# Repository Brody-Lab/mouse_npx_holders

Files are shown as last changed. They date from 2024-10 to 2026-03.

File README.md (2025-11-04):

# The Tuckbox - neuropixel 2.0 holders for chronic electrophysiology in mice
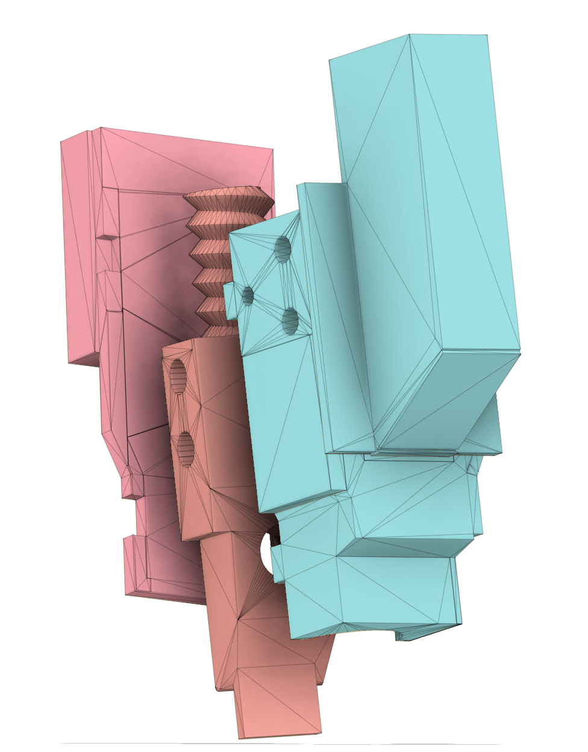
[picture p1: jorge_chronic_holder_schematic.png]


Printable files for Jesse Kaminsky's chronic neuropixel holders. All designs were modified in tinkercad from the original holders used for rats found in [this repo](https://github.com/agbondy/neuropixels_2.0_implant_assembly). Because of this I currently only have mesh files for these designs, and no true 3d structural file. Someday I'll learn an actual 3D modelling software...

Assembly instructions are [here](https://github.com/Brody-Lab/mouse_npx_holders/blob/main/Neuropixels%202.0%20Implant%20Assembly.pdf).

Production 2.0 internal holder modified in collaboration with [Rob Fetcho](https://scholar.google.com/citations?user=SHq1IlIAAAAJ&hl=en).

Narrower versions of production 2.0s by [Jorge Yanar](https://scholar.google.com/citations?user=Estf_eEAAAAJ&hl=en).

There is also a version of the [narrower holders with a cap](https://github.com/Brody-Lab/mouse_npx_holders/tree/main/production%20npx/npx2%20production%20narrow%20with%20cap), allowing complete protection of the probe/flex without any protective wrapping (for single-housed mice).

For other holders (that were designed for mice from the start) please see [this awesome resource](https://github.com/Julie-Fabre/awesome_neuropixels).

Feel free to contact me about these designs with any questions at jkaminsky@princeton.edu

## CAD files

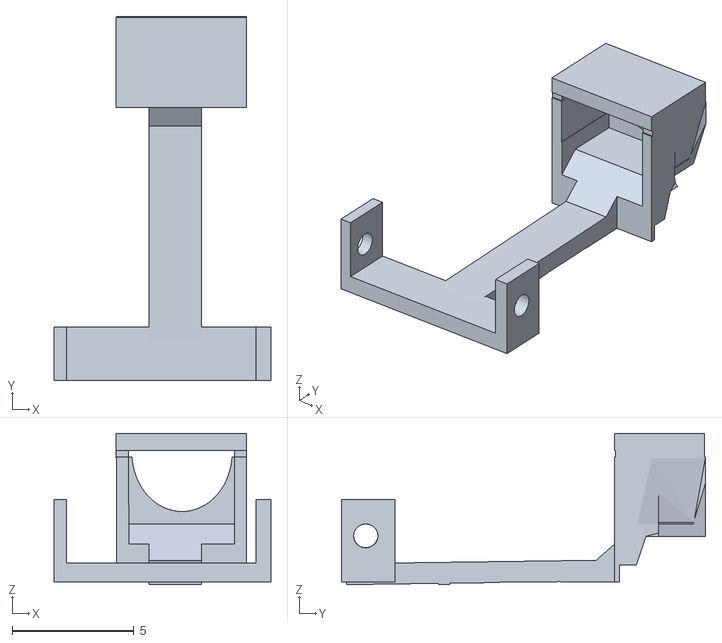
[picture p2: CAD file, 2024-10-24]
pre-production npx (phase 2b)/npx beta external frame.stl
8.90 x 14.9 x 6.20

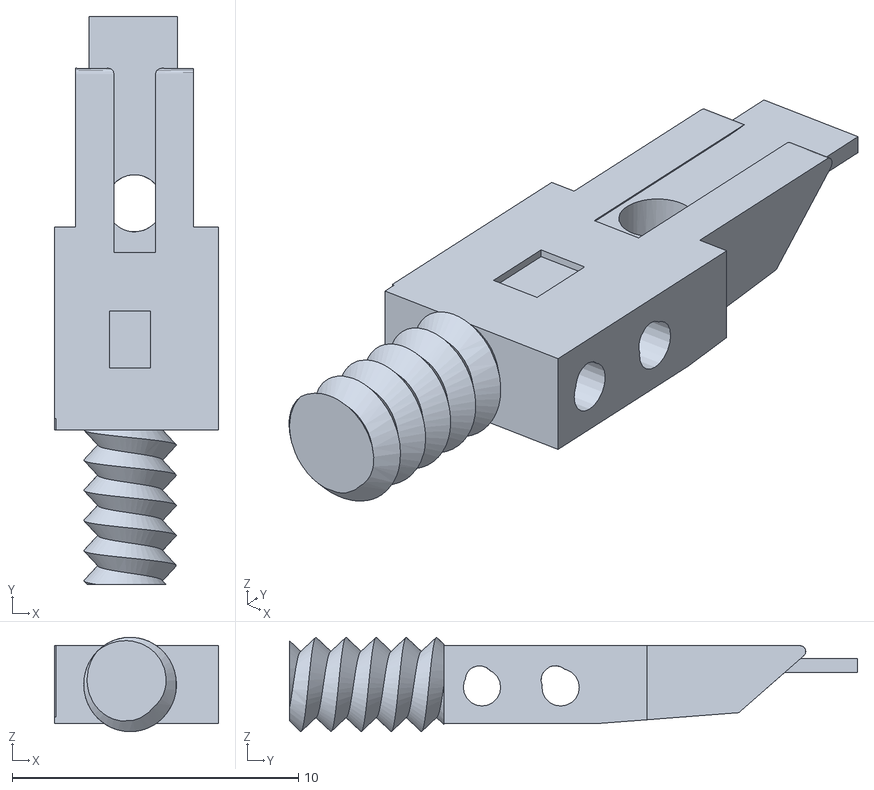
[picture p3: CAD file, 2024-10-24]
production npx/npx2 production internal jesse.stl
5.75 x 19.9 x 3.30

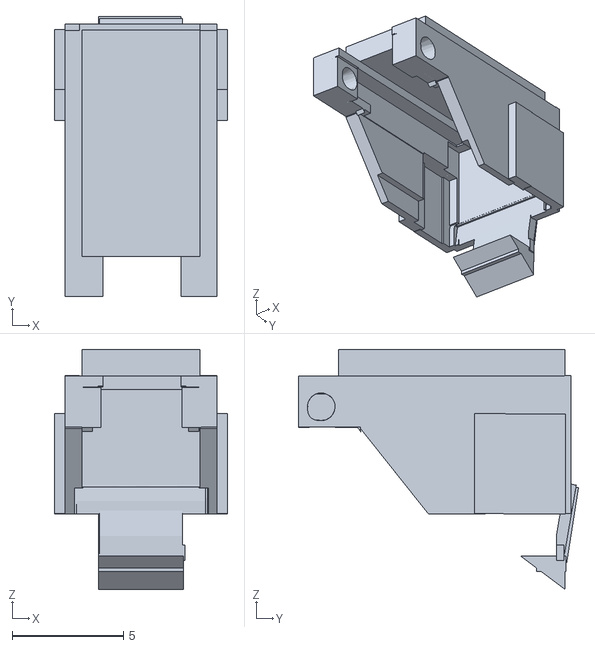
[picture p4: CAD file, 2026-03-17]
production npx/npx2 production narrow with cap/cap_v2.stl
7.80 x 12.6 x 10.8

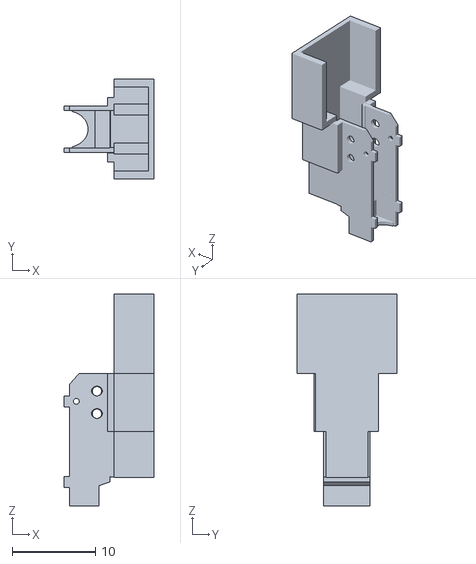
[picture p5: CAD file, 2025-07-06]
production npx/npx2 production narrow/Narrow production v6 external head stage.stl
10.8 x 12.0 x 25.4

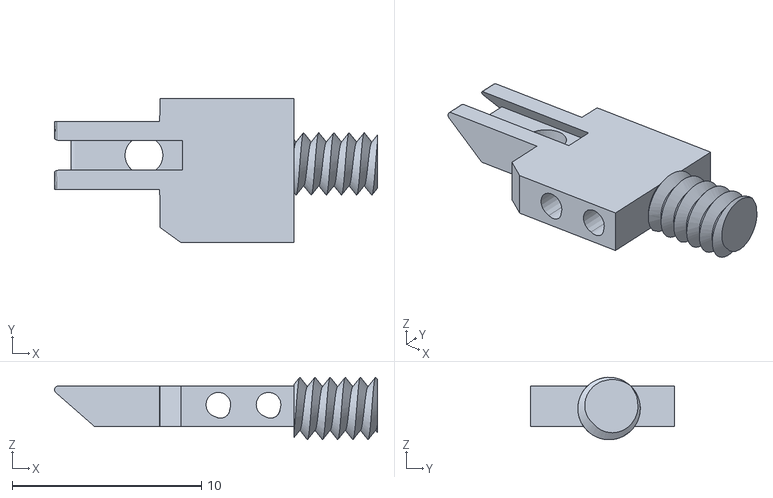
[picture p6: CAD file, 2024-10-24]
pre-production npx (phase 2b)/npx beta internal.stl
17.0 x 7.60 x 3.30

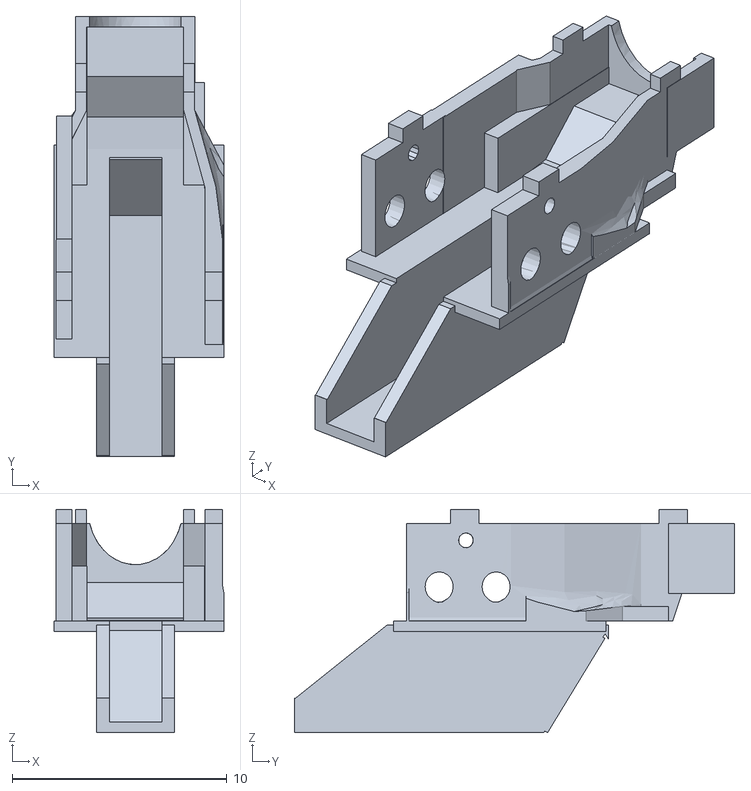
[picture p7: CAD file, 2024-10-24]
production npx/npx2 production external jesse.stl
7.90 x 20.5 x 10.4

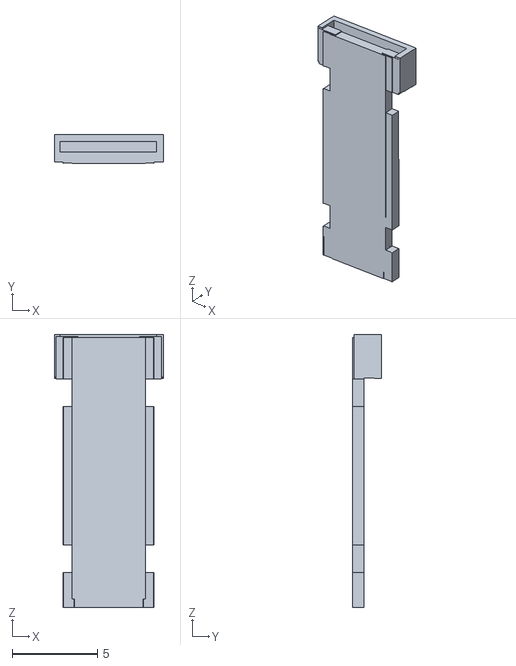
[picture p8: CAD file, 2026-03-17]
production npx/npx2 production narrow with cap/lid_v2.stl
6.40 x 1.70 x 16.0

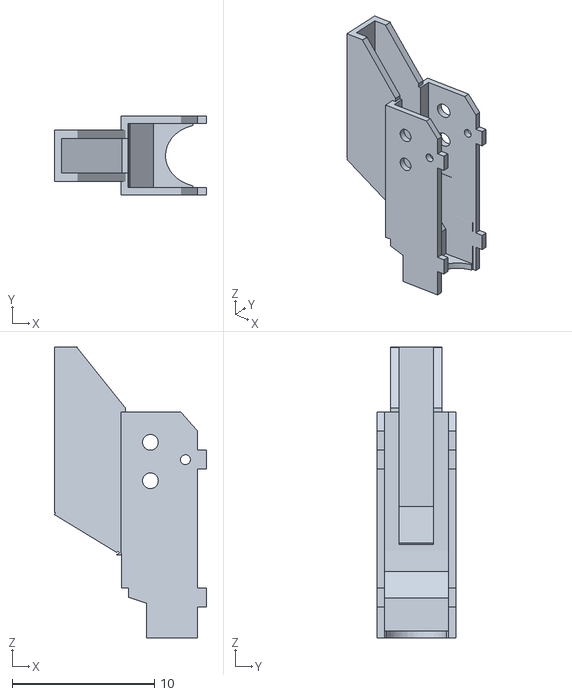
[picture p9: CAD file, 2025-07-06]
production npx/npx2 production narrow/Narrow production v6 external large tuckbox.stl
10.7 x 5.54 x 20.4

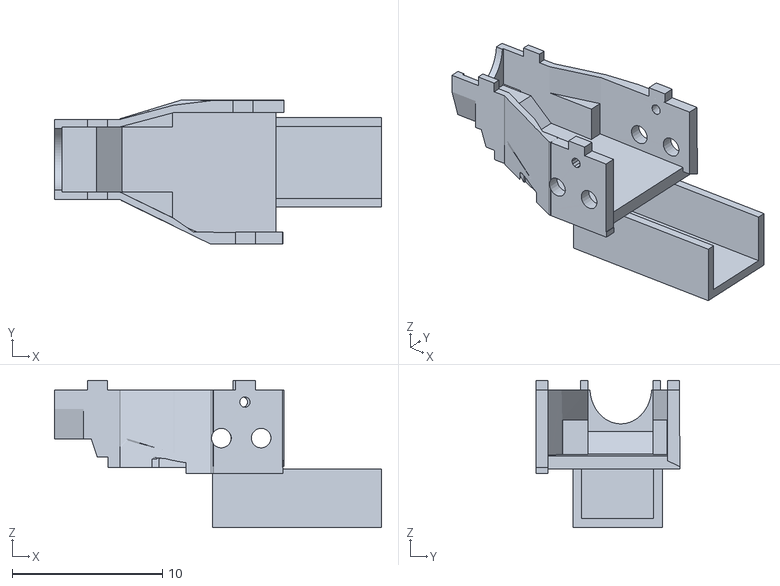
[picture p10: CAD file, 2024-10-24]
pre-production npx (phase 2b)/npx beta external.stl
21.7 x 9.60 x 9.79

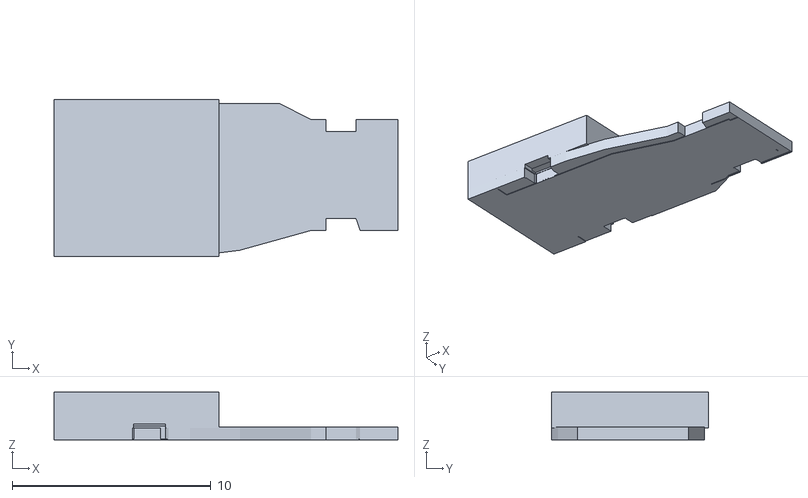
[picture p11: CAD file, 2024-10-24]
production npx/npx2 production lid jesse.stl
17.3 x 7.90 x 2.40

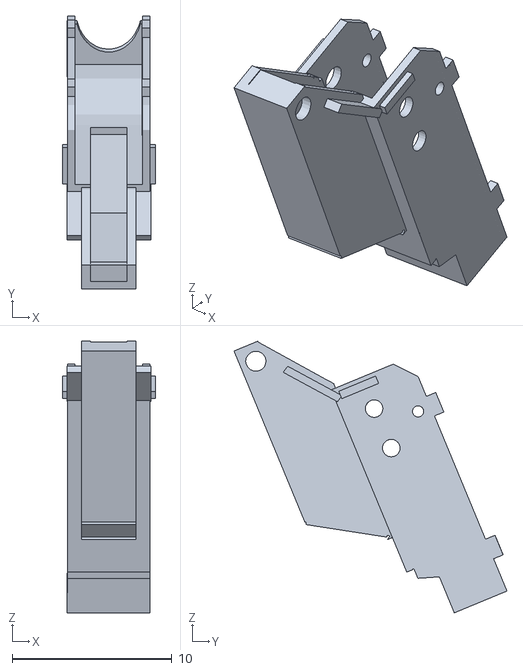
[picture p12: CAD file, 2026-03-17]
production npx/npx2 production narrow with cap/external_v2.stl
5.80 x 17.1 x 17.0

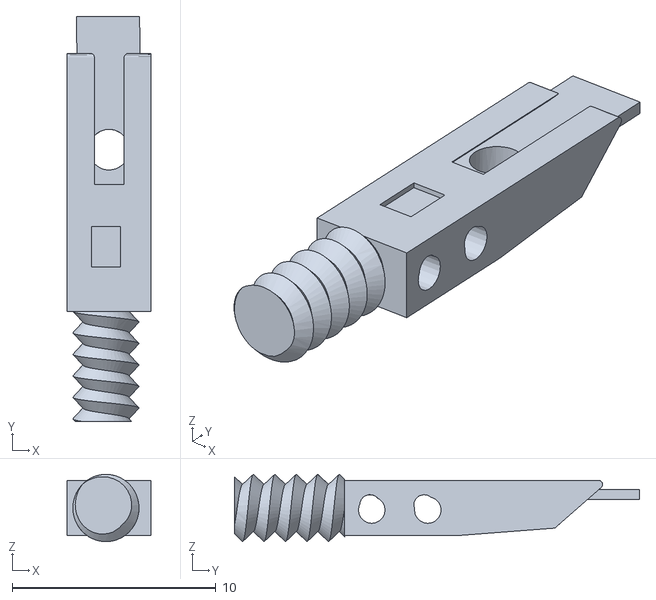
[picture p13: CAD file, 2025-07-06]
production npx/npx2 production narrow/Narrow production v7 internal.stl
4.12 x 19.9 x 3.30

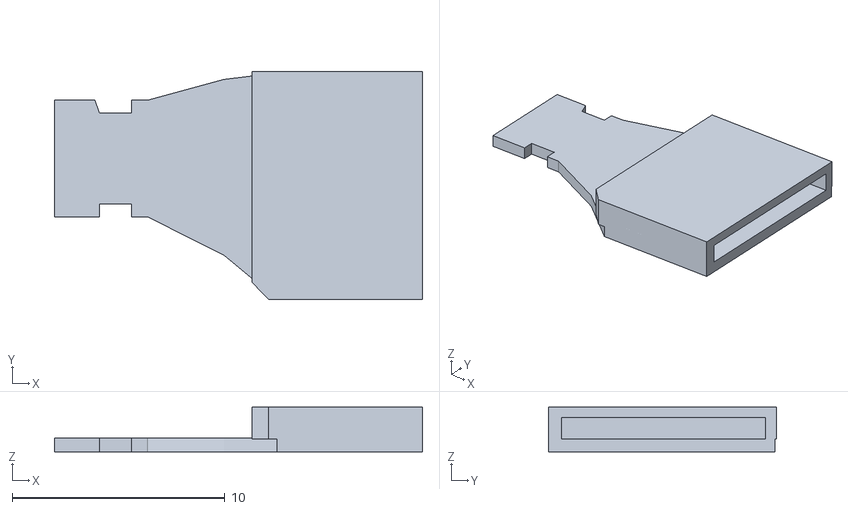
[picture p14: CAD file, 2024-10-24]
pre-production npx (phase 2b)/jesse_beta_lid_trimmed.stl
17.3 x 10.7 x 2.10

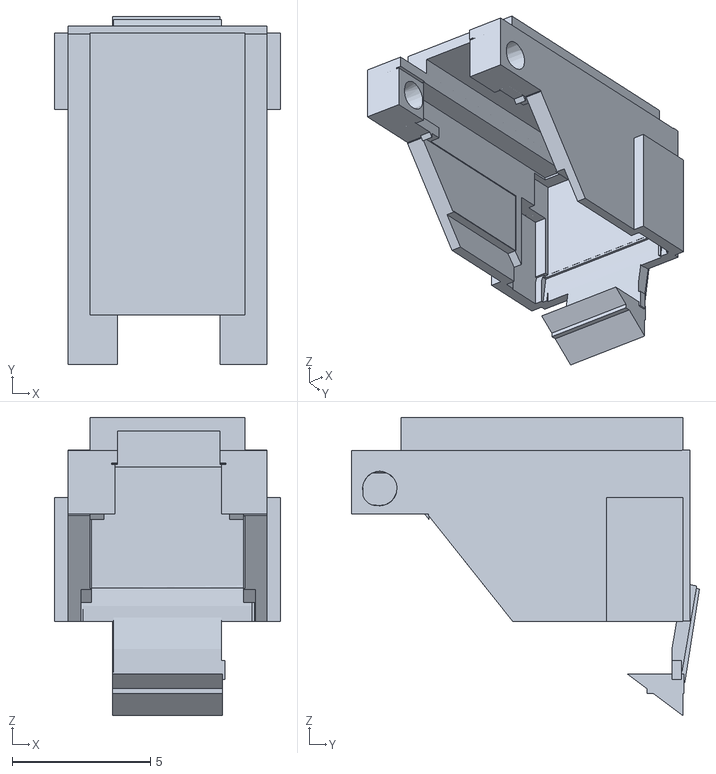
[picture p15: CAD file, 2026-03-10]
production npx/npx2 production narrow with cap/cap.stl
8.20 x 12.6 x 10.8

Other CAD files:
production npx/npx2 production narrow/Narrow production v6 lid.stl
production npx/npx2 production narrow with cap/cap front.stl
production npx/npx2 production narrow/Narrow production v6 external.stl
production npx/npx2 production narrow with cap/cap external.stl
production npx/npx2 production narrow with cap/cap internal.stl

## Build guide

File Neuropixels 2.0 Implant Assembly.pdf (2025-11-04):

# Neuropixels 2.0 Implant Assembly

written by Sarah Jo Venditto for an older version of this holder
updated by Jesse Kaminsky for his version
photo credits to Joseph LaBarbara, who was getting into photography so I gave him an excuse to use his new fancy camera

## Materials

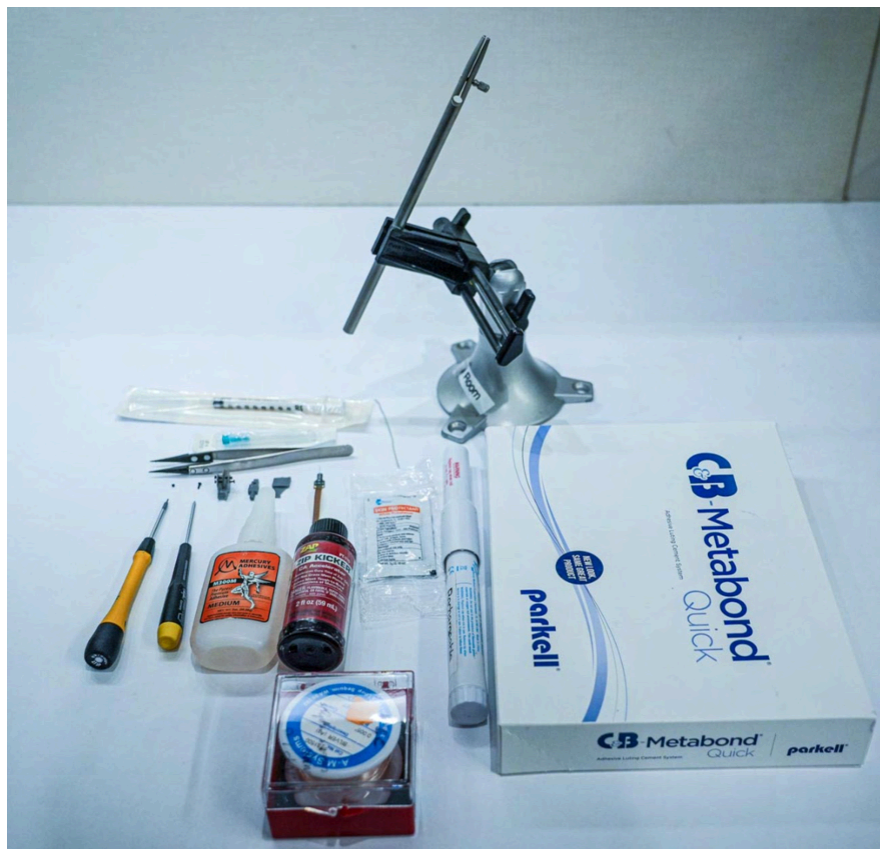
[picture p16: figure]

- 3D print:
https://github.com/Brody-Lab/mouse_npx_holders/tree/main/production%20npx
- grey V5 resin. 0.05mm resolution or finer
- don’t use the auto-orient button in preform, see here for our suggested way to orient each piece. (https://github.com/Brody-Lab/mouse_npx_holders/blob/main/production%20npx/npx2%20production%20narrow/tuckbox_narrow_v6.form)
- if possible, use small wire to clear out holes before curing (washing on high speed usually takes care of this)
- probe holder parts:
- external chassis (https://github.com/Brody-Lab/mouse_npx_holders/blob/main/production%20npx/npx2%20production%20external%20jesse.stl)
- internal holder (https://github.com/Brody-Lab/mouse_npx_holders/blob/main/production%20npx/npx2%20production%20internal%20jesse.stl)
- tuckbox lid (https://github.com/Brody-Lab/mouse_npx_holders/blob/main/production%20npx/npx2%20production%20lid%20jesse.stl)
- versions for using a cap instead of coban (https://github.com/Brody-Lab/mouse_npx_holders/tree/main/production%20npx/npx2%20production%20narrow%20with%20cap)
- assembly tools:

- box for holding everything and to give you a sense of ownership (https://www.mcmaster.com/4629T2/)
- bovie cautery (https://global-medical-solutions.com/Bovie-HIT1-Change-A-Tip-High-Temperature-Power-Handle_p_1183.html)
- PH00 phillips screwdriver (https://www.mcmaster.com/7440A21/)
- 0.9 (0.035") hex screwdriver (https://www.mcmaster.com/7440A75/)
- wire cutter for 3d printed parts (https://www.amazon.com/Hakko-TR-20-SM-Flush-cut-Construction-21-Degree/dp/B00FZPH7WO?s=hi)
- screws (https://www.amazon.com/dp/B073K19THX)
- set screw (https://www.mcmaster.com/92695A005/)
- bolt cutter/dremel, anything that can cut thin metal rods (https://www.amazon.com/gp/aw/d/B0D9J45B24/?aaxitk=b1420fe8e2df99e2bdb43f9670d1424f&hsa_cr_id=0) (only if using cap)
- box for assembled probes
- static control box (https://www.mcmaster.com/catalog/130/2059/4715T61)
- antistatic foam (cut lines in it to wedge the probes in) (https://www.mcmaster.com/87035K42/)
- other stuff:
- vise clamp with base (https://www.amazon.com/PanaVise-Model-201-Junior-Miniature/dp/B000B61D22)
- cannula holder (https://kopfinstruments.com/product/model-1766-ap-cannula-holder/)
- 0.005'' silver ground wire (https://www.a-msystems.com/p-756-bare-silver-wire.aspx)
- soldering iron (https://www.weller-tools.com/us/en/industrial-soldering/products/soldering-irons)
- solder (https://www.digikey.com/en/products/detail/chip-quik-inc/SMDSWLF-006-50G/8681844)
- white petroleum (https://www.amazon.com/Globe-Petrolatum-Petroleum-Soothing-Irritations/dp/B0BS76NJ73)
- 60ga drill bit (https://www.mcmaster.com/8907A17/)
- thin cyanoacrylate glue (https://www.amazon.com/Mercury-Adhesives-Starter-Pack-accelerator/dp/B06X6MBZ3C) & zip kicker, (https://www.dickblick.com/items/zip-kicker-ca-accelerator-spray-bottle-refill-8-oz/?clicktracking=true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) (and thick glue if using cap)
- 1mL syringe (https://www.fishersci.com/shop/products/bd-slip-tip-sterile-syringes-3/14823434) w/ long needle (https://www.fishersci.com/shop/products/bd-general-use-precisionglide-hypodermic-needles-20/1482649) for zip kicker
- grey tip needle (https://www.fishersci.com/shop/products/bd-general-use-precisionglide-hypodermic-needles-20/1482648)
- cotton swabs (https://www.uline.com/Product/Detail/S-18991/First-Aid/Cotton-Tipped-Applicators-Industrial-6)
- weigh boats (https://www.amazon.com/Weigh-Boats-Medium-Disposable-Anti-Static/dp/B07M5RMNPF)
- metabond (https://www.parkell.com/C-B-Metabond-Quick-Adhesive-Cement-System)
- metal rods (https://www.amazon.com/VictorsHome-Stainless-Crafts-Helicopter-Airplane/dp/B09634W3JQ?hvadid=580811217033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) (only if using cap)

## Pre-probe: holder parts set-up

- do all of this before getting the probe!
- remove supports from 3D printed parts
- sand down any jagged edges if necessary. however, if you angled your parts correctly there shouldn't be any support inside the probe holder that would prevent the parts fitting together. Check anywhere that parts will be in contact with each other.
- always have extras in case anything breaks
- drill out holes on external holder AND internal holder* using the 60ga drill bit
- this is only necessary if the holes did not print nicely. with modern formlabs resin printers and high speed washing I have never had to do this.
- make sure the screw starts twisting through the external holder and into the internal holder so that you're not met with too much resistance when the probe holder is assembled (no need to screw it in all the way, you don't want to risk stripping the holes)

- you can leave the screws in the external chassis
- use the gray tip needle to clear out the smaller holes on the external holder for the ground wire if necessary
- *if using a new probe. use a dovetail connector from a broken probe and slide into internal probe holder until it slides on comfortably without excessive force.
- this will give you a feel of how it'll slide on before using a real probe
- make sure you can slide it on without needing to apply pressure to the shank end
- if it's too tight, try dipping the dovetail connector in IPA and sliding on until it loosens up
- prepare cannula holder in holding clamp
- cut ground wire, ~3 in., long enough to reach from the probe holder to wherever your
| ground will be (err on the longer side, you can always trim it down)
- only if you are using the cap version
- cut the metal rods into 7mm long
| pieces with bolt cutters or a dremel
| (it’s okay if the measurement is off by
| a little bit either way, but don’t use any
| >1mm short). I usually just cut a
| bunch in advance.
- align the hinge holes on the cap with
| the holes at the very top of the
| external (version for the cap)
- insert the 7mm metal rod and ensure
| it is fully sitting in the opposite side of
| the cap. It should be sticking out just
| a tiny bit still from where you inserted
| it.
- Apply a tiny bit of thick cyanoacrylate
| glue to the exposed metal rod and
| then fix it with a tiny bit of zip kicker.

## Assemble the internal holder

- grab probe

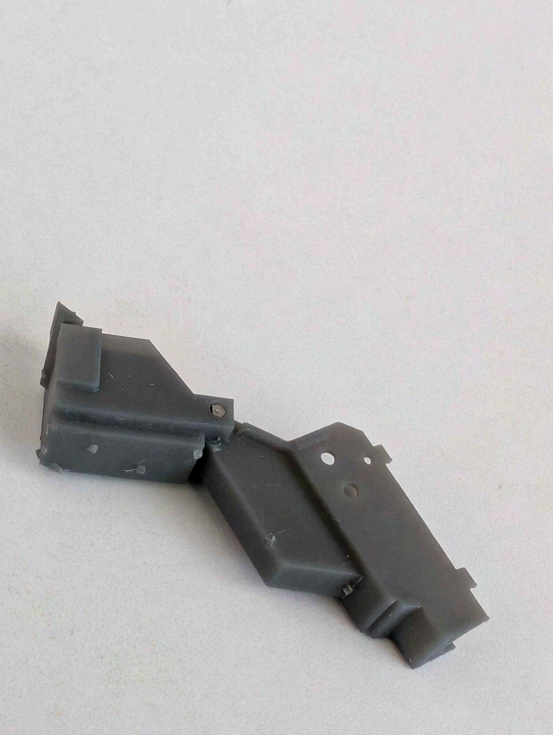
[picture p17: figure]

- try to always work with the probes facing away from you
- NEW PROBE:
- place internal holder into cannula holder, dovetail connector side up
- carefully remove probe from neuropixels box (make note of the serial number) ■ spread apart encasing foam with one hand. take care that no foam is
| caught on the probe that might hinder it from being lifted out
■ slowly and gently pull out probe using plastic or ceramic tip forceps in
| other hand. again, be careful that the probe isn't caught on the foam

■ once the probe is free from the foam, carefully grab with a gloved hand
- carefully slide the probe into the internal holder
■ watch the tips of your fingers. make
| sure they don't get too close to the end
| near the probes
■ you can apply gentle pressure to the
| ribbon cable or press back on the sides
| of the circuit board to slide it on all the
| way
■ when it is fully in, you should only see
| the silver dovetail metal when you look
| through the set screw hole on the
| opposite side
- feed the ground wire through the reference
holes at the base of the ribbon cable near the
probe

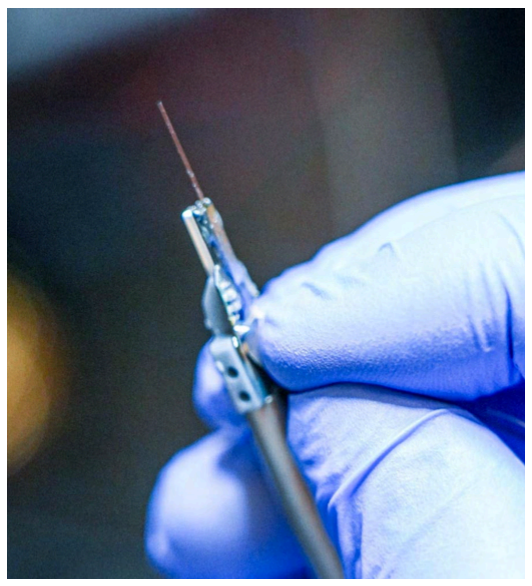
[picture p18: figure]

■ they will be pressed against the internal holder, so carefully feed in using forceps
■ you may need to gently lift the ribbon cable to provide space to feed in the
| wire
■ only pull so much through so that the majority of the wire is on one side.
| the long side doesn't matter, but it can be helpful to have the longer side
| on whatever side will point towards the ground during implantation
■ be careful of the loose ground wire. make sure it doesn't hit the shanks
- turn on the soldering iron and wait to heat up
- quickly and carefully solder the ground wire to the probe
■ you can cut down the wire on the short side
■ you can also cut the outer segments of the ribbon cable above the
| soldered point

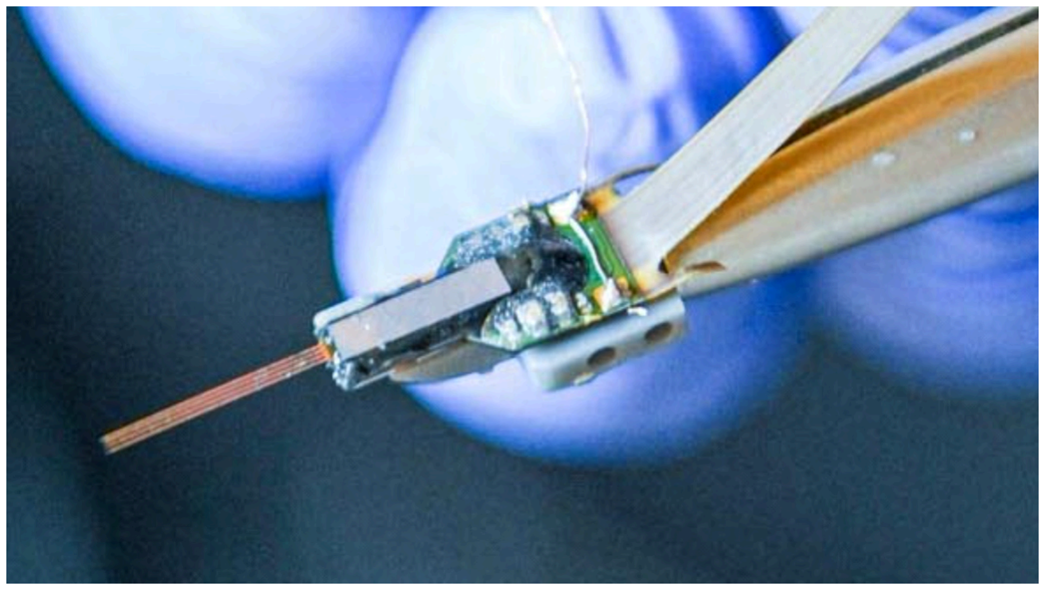
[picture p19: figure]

- flip the probe around, set screw side up
- make sure the probe is pushed all the way into the internal holder, and screw in the set
| screw
- screw in as perpendicular as possible to the internal holder
- initial screwing will be met with a bit of resistance as it taps the threads
- the resistance will greatly increase once the set screw meets the metal face of
| the probe's butterfly connector. this is when you can stop screwing down, and will
| occur when the set screw is flush with the internal holder (it should be just
| slightly below, not protruding at all).
- if you screw past this point, the pressure will release as you strip the threading. if
| this occurs, set up a new internal holder

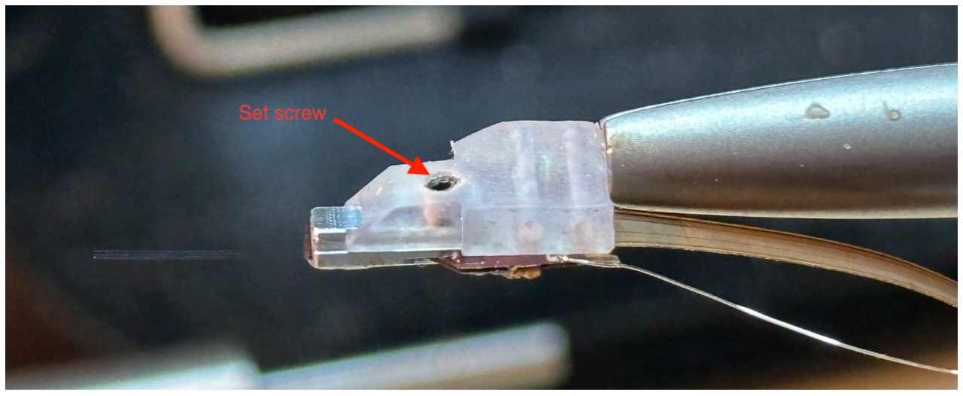
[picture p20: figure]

- REUSED PROBE
- make sure the probe has been resterilized
- you can use the old probe holder, but first test that the probe is still secured firmly
| with the set screw.
- if you're worried about the integrity of the used internal holder, release the set
| screw and carefully remove the probe. prepare a new internal holder and follow
| the steps above
- for the ground wire: the old ground wire would have been sheared from
| extraction, so a new length of silver wire will need to be attached to one of the
| reference sites. just use additional solder to connect the new length of wire to the
| old solder point

## Assemble the external chassis

- orient the probe such that the ground wire side is facing up
- feed the ground wire through the small hole between the screw holes on the external
| chassis and pull it through while fitting the internal holder into the external chassis

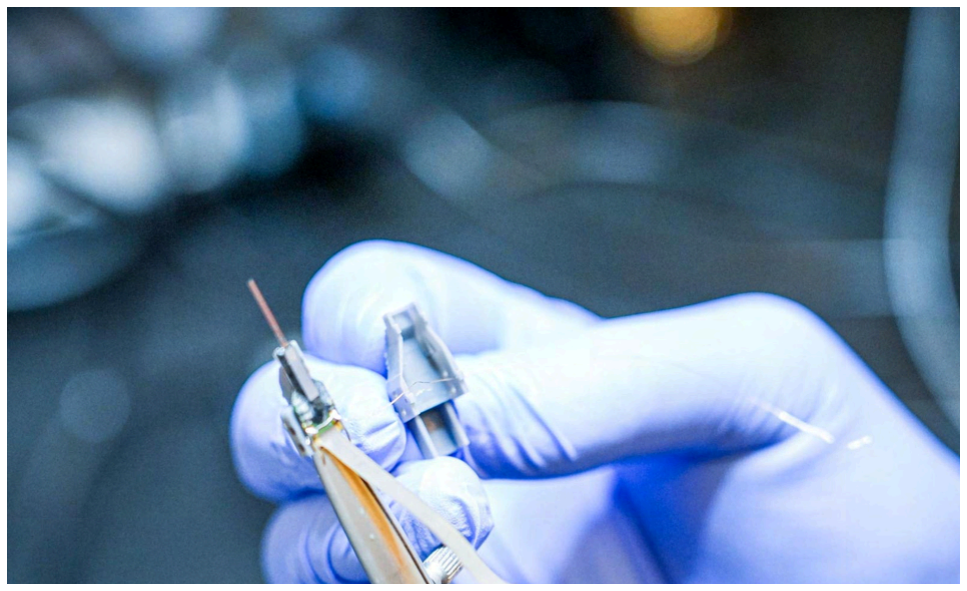
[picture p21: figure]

- align the external chassis such that the screw holes align with the internal holder (should
| be coming from underneath the probe)
- screw in the four adjoining screws
- I won't always screw it in all the way, but you might want to so that the sides of
| the external holder are pressed up tight to the external top
- you can optionally put the lid on, without gluing it, to allow you to grip the implant better as you screw

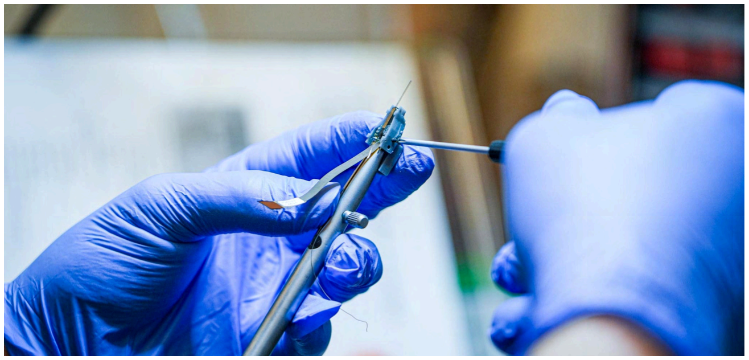
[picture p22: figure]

- If you will be soldering a gold ground pin to the end of the ground wire, do it now.
- fit the external top on top of the external chassis.
- prepare the zip kicker in the 1mL syringe and pour some thin cyanoacrylate glue into a
| weigh boat

- snap a cotton swab in half to create a sharp
| edge in the wooden shaft to apply the glue
| (alternatively, use a large needle tip)
- separately glue each long edge of the
| external top to the external chassis
- angle up one edge (you can also
| point the shanks more upward to
| direct run-off glue downwards
| instead of inwards)
- firmly press the external top with the
| external chassis, making sure edges
| are flush with no gaps
- dip the wooden stick into the glue
| and paint along the upward edge
| connecting the external top to the
| external chassis
■ | you want enough to seal the
| pieces together, but you don't
| want any to pour into the
| external chassis and onto
| the internal holder.

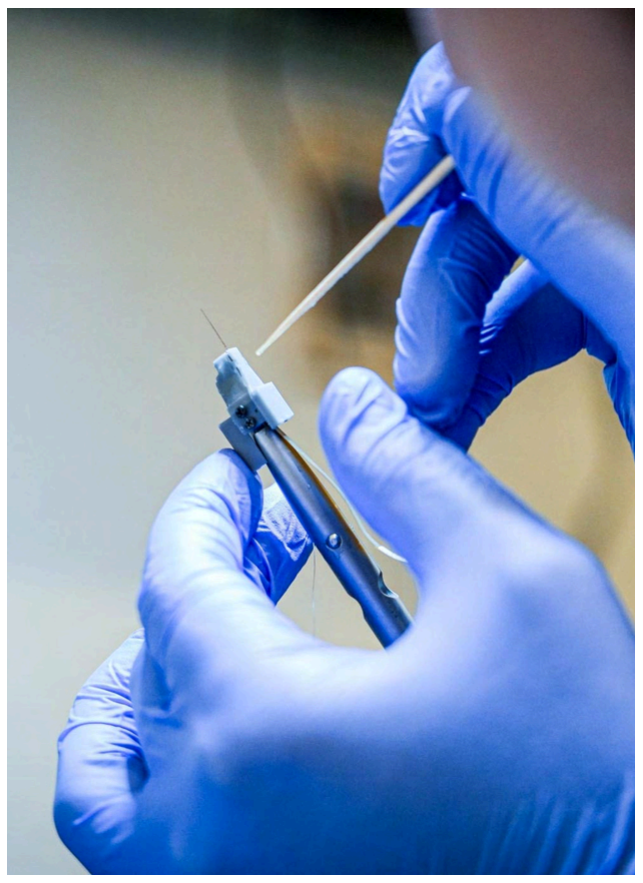
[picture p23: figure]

- place a drop of zip kicker onto the glue for fast curing
- angle up the other edge and repeat
- unscrew the internal holder and gently slide off the external chassis to make sure the external chassis isn't glued to the internal holder. screw back together
- if you do this soon
enough after applying the zip kicker, you can still dislodge it if a little gets through
- be careful not to shear
the ground wire while moving the external chassis
- when screwing it back in, I still like to leave ~1mm sticking out. I

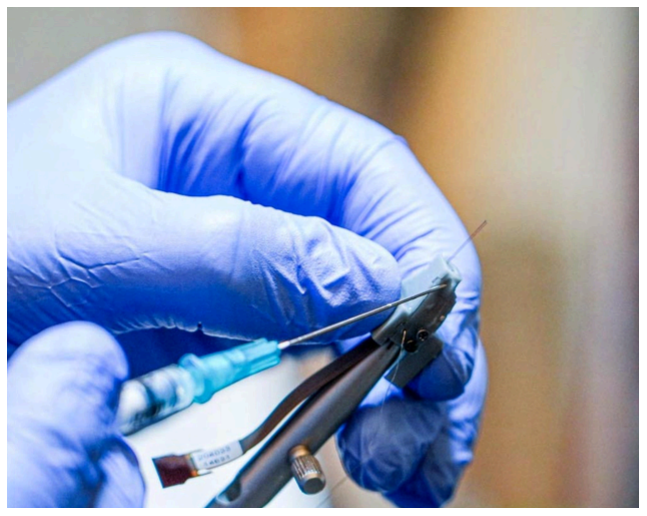
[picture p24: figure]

| won't screw it in completely until after applying metabond to make sure
| metabond doesn't cover the screw caps

## Finishing touches

- orient the probe so the shanks are
| facing up at an angle
- using a clean tube of white
| petroleum and the cautery, melt
| small drops of petroleum onto the
| base of the shanks
- be careful not to touch the
| probes or get too close
| with the cautery
- it's ok for petroleum to flow into the probe holder
- build up the petroleum around the
| base of the shanks

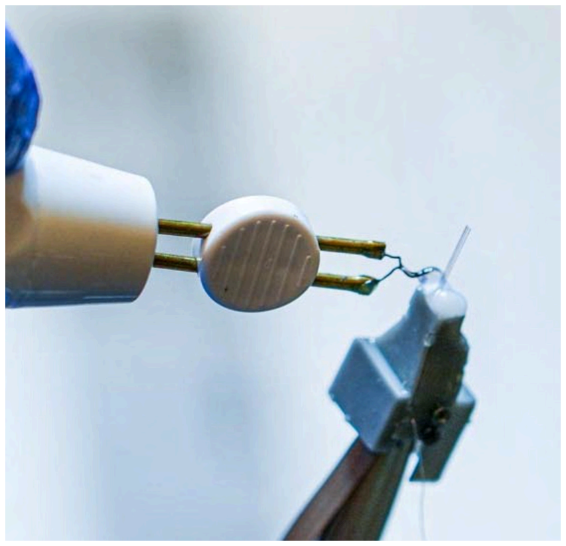
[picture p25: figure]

- I will alternate probe angles so that melted drops will flow down from both sides of the base
- the height of the mound will depend on how far you want to insert the probe during surgery. you can build up high enough such that after implantation, the petroleum is flush with the skull. or alternatively, there can be a tunnel of air between the petroleum and the skull that will be completely enclosed in cement.
- wipe any petroleum that may have dripped down the sides of the probe holder with
cotton swabs and IPA. there
should only be petroleum at
base where the shanks come

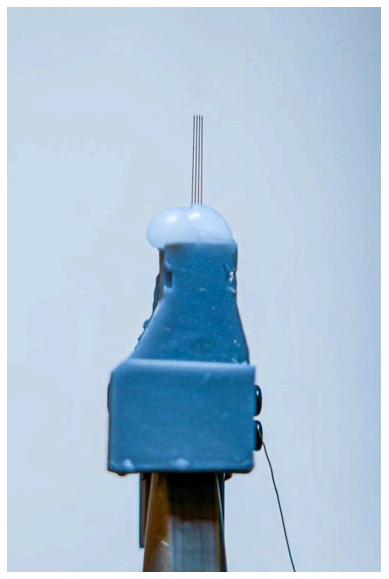
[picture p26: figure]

| out
- the petroleum should always be applied
| before the metabond because of this: we
| don't want petroleum residue compromising
| the metabond externally
- If you're brave, you can remove excess
| petroleum above the end of the holder with
| a thin wire, shearing each side into a flat
| face.

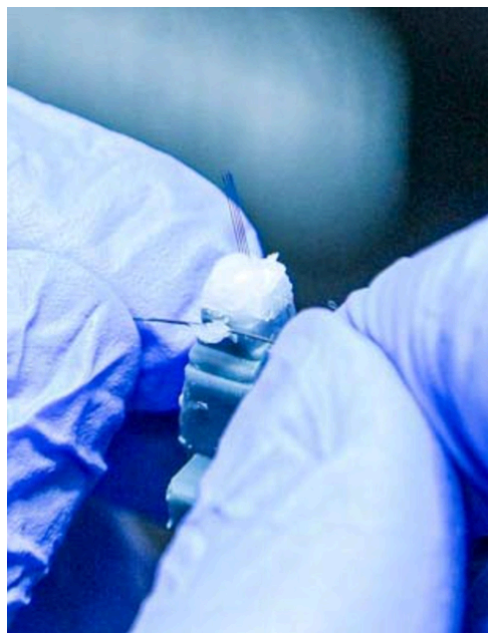
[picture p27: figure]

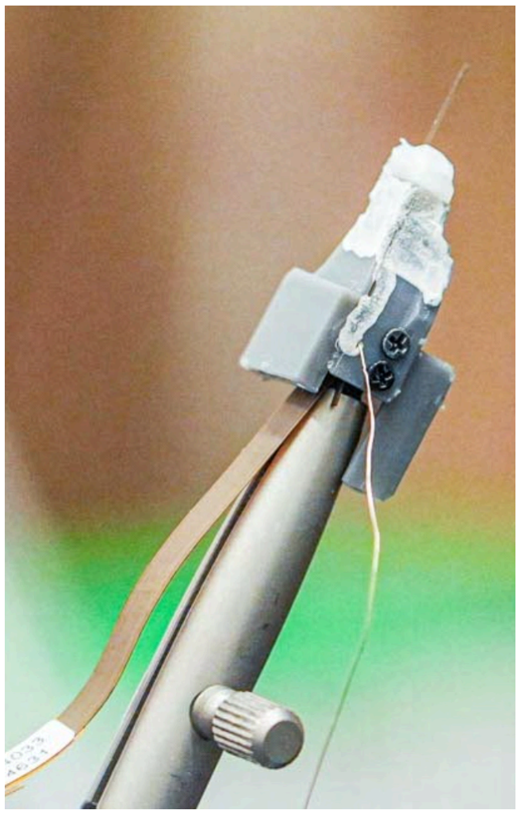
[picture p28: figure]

- prepare the metabond
- if you keep the mixing
| dish cold on an ice pack,
| you can extend the
| working time of the
| metabond and mix it all
| together in a single well
- paint all sides of the external
| holder with metabond
- most important to cover
| the lower halves that will
| make contact with the
| acrylic
- fill in the ground holes on
| both sides
- avoid the screw holes
| (this is where having
| them slightly unscrewed
| will help)
- after the metabond dries,
| carefully place the finished
| probe holder in a probe holder
| box
- test the probe in an ephys rig to
| make sure everything is
| working

## Video showing how to tuck in the flex (applies to both cap

and regular version) (https://drive.google.com/file/d/14n-fH7Hn-LWftiRLUzeRkK8pd_DkS8_v/view?usp=sharing)

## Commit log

2024-10-24 initial commit of 3D files
    [jesse_beta_lid_trimmed.stl, npx beta external frame.stl, npx beta external.stl, npx beta internal.stl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]
2024-11-13 add narrow version of npx2 production
    [Narrow production v4 external large tuckbox.stl, Narrow production v4 external.stl, Narrow production v4 internal.stl, Narrow production v4 lid.stl]
2024-11-14 increase narrow lid-external juncture size
    [Narrow production v4 lid.stl]
2025-01-07 added prototype version with cap
    [cap external.stl, cap front.stl, cap internal.stl, cap.stl]
2025-01-10 made cap slightly larger
    [cap external.stl, cap front.stl, cap internal.stl, cap.stl]
2025-01-10 FIX: npx2 production narrow internal was accidentally stretched 0.5mm
    [Narrow production v4 internal.stl, Narrow production v6 external large tuckbox.stl, Narrow production v6 external.stl, Narrow production v6 internal.stl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]
2025-05-05 added two holes to narrow external large tuckbox
    [Narrow production v6 external large tuckbox.stl]
2025-05-05 added two holes to external narrow cap
    [cap external.stl]
2025-06-06 added implant assembly instructions
2025-06-06 added narrow external that can hold head stage
    [Narrow production v6 external head stage.stl]
2025-07-06 fix small stretch in narrow production internal, update .form file
    [Narrow production v6 internal.stl, Narrow production v7 internal.stl]
2025-08-12 increased cap hinge size
    [cap external.stl, cap.stl]
2025-08-13 updated cap spacing
    [cap.stl]
2025-08-15 adjusted cap clasp tightness
    [cap.stl]
2025-10-21 increased cap capacity
    [cap external.stl, cap front.stl, cap.stl]
2025-11-04 assembly instructions for cap
2025-11-04 deleted old assembly instructions
2025-11-04 fixed assembly instructions link
2026-03-03 slightly shrunk cap front
    [cap front.stl]
2026-03-06 extended cap latch
    [cap.stl]
2026-03-10 adjusted cap spacing
    [cap.stl]
2026-03-17 narrower cap pieces
    [cap_v2.stl, external_v2.stl, lid_v2.stl]
